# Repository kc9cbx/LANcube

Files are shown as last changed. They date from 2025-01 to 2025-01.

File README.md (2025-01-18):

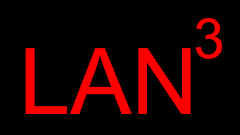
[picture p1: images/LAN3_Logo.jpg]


LAN3 is based on the design by Martin Aubé - 
[GitHub](https://github.com/aubema/lancube) - [WiKi](http://obsand.org/wiki/index.php?n=Prof.LANcube) - 
[Licensed under CC BY-SA 4.0 ](https://creativecommons.org/licenses/by-sa/4.0/)

## What is it?
LAN3 is a device that is designed to sample spectral and directional properties of lightsources in the urban or natural environments. In other words, it allows you to place this device on top of your vehicle, drive around and capture exeact phyisical location of each light source along the way, characterize each light's color temperature, and its spectrum. 

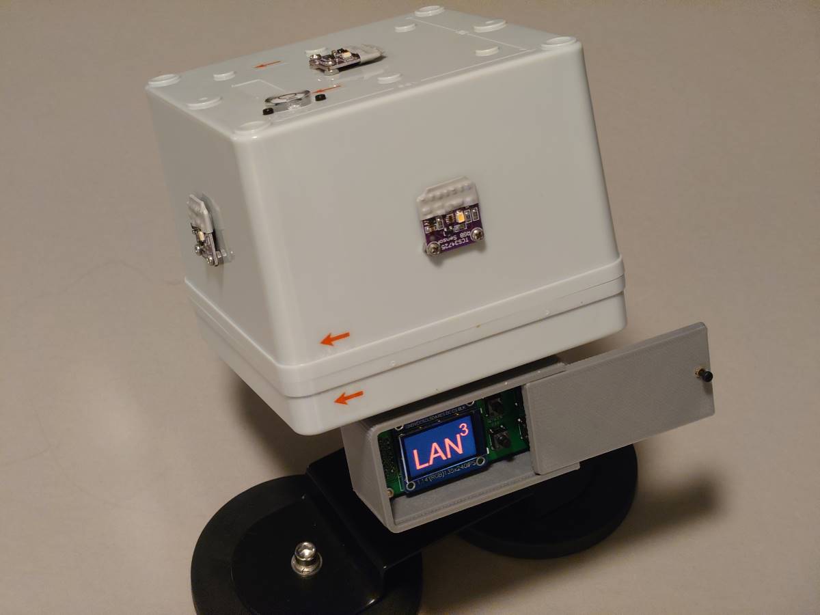
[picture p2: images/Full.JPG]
Full


## Changes in this version
This version of LAN3 exapands the original design with the follwing changes:
### Hardware Changes 
 - Addtion of the control panel - display and 4-button interface.
 - Addition of newly designed PCBs for both the control panel and the main part of the device.
 - Replacement of the external enclosure with the off-the-shelf box.
 - Transition to use of internal battery and battery monitoring for standalone operation.
 - Integration of the GPS on the interior of the device.

### Software Chages
 - Moving web server from Apache to Nginx.
 - Implementation of GPSd.
 - Automated time sync wiht GPS.
 - Addtion of full-featured web interface including device control, status management, and file management.
 - Change of how GPS status was reported from counting number of satelies to GPS mode. 
 - Requiring GPS Mode 3 (3D lock/high precision) to capture valid data.
 
## Build
The LAN3 is designed with off-the-shelf parts, available from Amazon, Ali Express, and may other places that sell DIY electronic components.

If you would like to build your own, head over the [Hardware](./Hardware/) section. There, you will find list of all the components, gerber files for PCBs, STL file for 3D printed part of the enclosure, and the assembly instructions.

For the software, pre-made IMG file is available that can be expanded onto an SD card. The [Software](./Softwre/) section has the details on how to provision your LAN3, allowing you to set your host and hotspot name. 

## Use
New interface is designed to make in-the-field data capture very simple:
1) Place the LAN3 on top of the vehicle. If possible, use a thin, dark fabric under the LAN3 to eliminate reflected light from impacting the measurements.
2) Press the "Power On" button.
3) Allow LAN3 to boot, to get a GPS lock, and to sync the time. The display will show "GPS Lock: Yes" and "GPS Time: Yes" when this is complete.
4) Press the "Start Measurement" button. The status on the display will show "Measuring".
5) Drive slowly around the area that you want to measure.
6) Once complete, press the "Stop Measurement" button.
7) Connect to the LAN3 hotspot, open your browser, go to the IP address on the LAN3 display, head over to the Files section, and download the file containing your measurements. 

## Data
Changes in this version of LAN3 were primarly focused on hardware and some of the software that supports that hardware. The core process of data capture has not changed. For data analysis and mapping after data has been captured, you will need to use the original LANCube analysis scripts. These are available on Martin Aubé's [GitHub](https://github.com/aubema/lancube) and in the [Original LANcube Archive](./Original_LANcube_Archive/) folder of this repo.

### Sample LAN3 Data
| Sensor | Year | Month | Day | Hour | Minute | Second | Latitude  | Longitude  | Altitude | GPSMode | Gain | AcquisitionTime(ms) | ColorTemperature(k) | MSI  | lux   | Red  | Green | Blue | Clear | Flag |
|--------|------|-------|-----|------|--------|--------|-----------|------------|----------|---------|------|---------------------|---------------------|------|-------|------|-------|------|-------|------|
| S1     | 2024 | 1     | 24  | 0    | 44     | 20.71  | 41.895442 | -87.654126 | 183.2    | 3       | 60   | 307.2               | 5875                | 0.6  | 49.57 | 2444 | 3094  | 2428 | 8301  | OK   |
| S2     | 2024 | 1     | 24  | 0    | 44     | 20.71  | 41.895442 | -87.654126 | 183.2    | 3       | 60   | 153.6               | 7201                | 0.67 | 37.14 | 745  | 1146  | 957  | 2825  | OK   |
| S3     | 2024 | 1     | 24  | 0    | 44     | 20.71  | 41.895442 | -87.654126 | 183.2    | 3       | 60   | 307.2               | 7820                | 0.7  | 31.84 | 1255 | 1996  | 1718 | 5100  | OK   |
| S4     | 2024 | 1     | 24  | 0    | 44     | 20.71  | 41.895442 | -87.654126 | 183.2    | 3       | 60   | 153.6               | 2429                | 0.49 | 24.89 | 1943 | 1236  | 1010 | 4064  | OK   |
| S5     | 2024 | 1     | 24  | 0    | 44     | 20.71  | 41.895442 | -87.654126 | 183.2    | 3       | 60   | 614.4               | 5933                | 0.59 | 28.73 | 2413 | 3388  | 2573 | 8782  | OK   |
| S1     | 2024 | 1     | 24  | 0    | 44     | 21.34  | 41.895512 | -87.65423  | 183.2    | 3       | 60   | 307.2               | 6572                | 0.63 | 40.83 | 1575 | 2414  | 1904 | 6225  | OK   |
| S2     | 2024 | 1     | 24  | 0    | 44     | 21.34  | 41.895512 | -87.65423  | 183.2    | 3       | 60   | 153.6               | 7077                | 0.65 | 47.39 | 793  | 1376  | 1105 | 3314  | OK   |
| S3     | 2024 | 1     | 24  | 0    | 44     | 21.34  | 41.895512 | -87.654231 | 183.2    | 3       | 60   | 307.2               | 7521                | 0.69 | 31.48 | 1433 | 2048  | 1774 | 5321  | OK   |
| S4     | 2024 | 1     | 24  | 0    | 44     | 21.34  | 41.895513 | -87.654231 | 183.2    | 3       | 60   | 153.6               | 2318                | 0.47 | 27.5  | 2116 | 1338  | 1070 | 4353  | OK   |
| S5     | 2024 | 1     | 24  | 0    | 44     | 21.34  | 41.895513 | -87.654231 | 183.2    | 3       | 60   | 614.4               | 6043                | 0.59 | 31.5  | 2523 | 3678  | 2796 | 9374  | OK   |
| S1     | 2024 | 1     | 24  | 0    | 44     | 21.97  | 41.895512 | -87.65423  | 183.2    | 3       | 60   | 307.2               | 7359                | 0.67 | 31.95 | 1050 | 1864  | 1517 | 4697  | OK   |
| S2     | 2024 | 1     | 24  | 0    | 44     | 21.97  | 41.895512 | -87.65423  | 183.2    | 3       | 60   | 153.6               | 6482                | 0.61 | 50.89 | 841  | 1433  | 1095 | 3419  | OK   |
| S3     | 2024 | 1     | 24  | 0    | 44     | 21.97  | 41.895512 | -87.65423  | 183.2    | 3       | 60   | 307.2               | 7106                | 0.68 | 24.99 | 1214 | 1639  | 1403 | 4311  | OK   |
| S4     | 2024 | 1     | 24  | 0    | 44     | 21.97  | 41.895512 | -87.654231 | 183.2    | 3       | 60   | 153.6               | 2426                | 0.46 | 32.85 | 2324 | 1521  | 1202 | 4794  | OK   |
| S5     | 2024 | 1     | 24  | 0    | 44     | 21.97  | 41.895513 | -87.654231 | 183.2    | 3       | 60   | 614.4               | 6041                | 0.59 | 26.54 | 2178 | 3128  | 2395 | 7925  | OK   |

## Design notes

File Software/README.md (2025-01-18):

## Setting up software and provisioning the LAN3 

#### Preparing the Card
Download the zip file containing the LAN3 SD card image from the Releases. Unzip the image – resulting file will be around 3.5Gb 

Follow the process outlined here: https://raspberrytips.com/create-image-sd-card/ to expand LAN3 image on to the SD card. 
 
To validate that your SD card was created correctly. Insert it into the LAN3 device and power it on. Keep in mind that first boot after card is created will take a while as image will re-size itself to fit the card and then reboot. If your GONet hardware is working correctly and the SD card was imaged correctly, after a couple of minutes, the display will turn on and you will see, on the very first line, “PROVISION” followed by a version number. 
 
#### Provisioning
Press the power off button to turn off the device. Once all lights have turned off, remove the SD card and place it back in your computer.
 
Download and open the provided LAN3Config.conf file. In the file, update the text in the quotes on the first line. This will set the name for your LAN3. For example, to name the LAN3 MyLAN3001, the first line should look like this:
HostName="MyLAN3001"

At this time, only the first line is used, so you can disregard the rest of the file.
 
Once you have the LAN3Config.conf updated, copy it on your LAN3 SD card into /fsboot/.
 
Place the SD card into the LAN3 and turn it on. It may take several minutes for provisioning to complete, as multiple automatic reboots are required, so please be patient.
 
Once provisioning is complete, the display will come on and you will see your LAN3 name at the very first line, indicating that provisioning was successful.

#### Hotspot
After provisioning, LAN3 will create its own hotspot, with the same name as the LAN3. When this happens, using the examle from above, you will see “HOTSPOT: MyLAN3001” on the display. You can connect to that hotspot using the password “Remote4LAN3” (capitalization matters!)

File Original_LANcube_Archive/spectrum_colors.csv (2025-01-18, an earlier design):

r/g | b/g | i/g | ULOR | tech
2.64 | 0.60 | 0.07 | 0.03 | HPS
2.50 | 0.65 | 0.07 | 0.03 | HPS
2.79 | 0.59 | 0.16 | 0.03 | HPS
3.47 | 0.74 | 0.25 | 0.03 | HPS
2.50 | 0.77 | 0.11 | 0.03 | HPS
2.27 | 0.84 | 0.50 | 0.03 | HPS
2.21 | 0.67 | 0.07 | 0.03 | HPS
2.84 | 0.71 | 0.16 | 0.03 | HPS
0.87 | 0.98 | 0.22 | 0.05 | MH4000
0.80 | 0.54 | 0.15 | 0.10 | MV
1.01 | 0.57 | 0.36 | 0.10 | MV
5.43 | 0.64 | 0.17 | 0.00 | LED1500
1.94 | 0.42 | -0.11 | 0.00 | LED1650
1.64 | 0.38 | -0.08 | 0.00 | LED1650
3.87 | 0.47 | 0.13 | 0.00 | LED1800
2.65 | 0.43 | -0.10 | 0.00 | LED1800
2.37 | 0.44 | -0.15 | 0.00 | LED1800
3.42 | 0.51 | 0.03 | 0.00 | LED1800
2.91 | 0.49 | 0.01 | 0.00 | LED1800
1.85 | 0.56 | 0.03 | 0.00 | LED2200
1.99 | 0.75 | 0.04 | 0.00 | LED3000
1.87 | 0.69 | 0.02 | 0.00 | LED3000
0.81 | 0.51 | -0.11 | 0.00 | LED3500
1.04 | 0.77 | -0.03 | 0.00 | LED4000
1.00 | 0.67 | -0.06 | 0.00 | LED4000
0.95 | 0.58 | -0.09 | 0.00 | LED4000
1.21 | 0.89 | 0.02 | 0.00 | LED5000
0.99 | 0.84 | 0.02 | 0.00 | LED5500
0.60 | 0.81 | -0.09 | 0.00 | LED5500
3.38 | 0.83 | 3.65 | 0.30 | INC2550
2.79 | 0.82 | 2.37 | 1.30 | INC2550

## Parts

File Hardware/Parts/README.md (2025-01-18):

| Part                                                                                     | Quantity | Source(s)                                                                                                          |
|------------------------------------------------------------------------------------------|----------|--------------------------------------------------------------------------------------------------------------------|
| MAIN BOARD                                                                               |          |                                                                                                                    |
| Main Board PCB                                                                           | 1        | See Hardware folder for gerber files                                                                               |
| SparkFun LiPo Fuel Gauge (MUST GET FROM SPARKFUN, LOTS OF FAKE ONES ELSEWHERE)           | 1        | https://www.sparkfun.com/products/20680                                                                            |
| GT-U7 GPS Module                                                                         | 1        | https://www.amazon.com/gp/product/B08ZSMPPP6                                                                       |
| Flexible 15 pin Cable,150mm, 1mm Pitch (FPC/FFC type - same as raspberry pi HQ camera)   | 1        | https://www.amazon.com/dp/B07RWQQHKY                                                                               |
| 15 Position FFC, FPC Connector Contacts, Vertical - 1 Sided 0.039" (1.00mm) Through Hole | 1        | https://www.digikey.com/en/products/detail/amphenol-icc-fci/SLW15S-1C7LF/1002258                                   |
| Electronic Power Switch with Reverse Voltage Protection, LV                              | 1        | https://www.pololu.com/product/2808 OR https://www.digikey.com/en/products/detail/pololu-corporation/2808/10450608 |
| 330uF 25V 8X12MM Electrolytic Capacitors                                                 | 2        | https://www.amazon.com/gp/product/B09TQTV372                                                                       |
| Raspberry Pi 4 B - at least 2GB Model                                                    | 1        | https://www.sparkfun.com/products/15446                                                                            |
| 2x20 Extra Tall Stacking Headers for Pi                                                  | 1        | https://www.amazon.com/gp/product/B01EF42LTY                                                                       |
| JST XH 2.54mm 7 Pin Male Connector and 26AWG Female Connector Plug with Wire             | 5        | https://www.amazon.com/gp/product/B0CF26XWJ4                                                                       |
| Extra Tall Stacking Header for Raspberry Pi - 2x20  Header                               | 1        | https://www.amazon.com/gp/product/B01EF42LTY                                                                       |
| USB-C charger and Boost Converter Module                                                 | 1        | https://www.amazon.com/dp/B09YD5C9QC                                                                               |
| 11mm Heatsink  for Raspberry Pi 4 (P165-B)                                               | 1        | https://www.amazon.com/dp/B08N5VZN8R OR https://geekworm.com/products/p165-b                                       |
| JST-PH 2.0 Male and Female Connector Cable                                               | 1        | https://www.amazon.com/dp/B07NWD5NTN                                                                               |
|                                                                                          |          |                                                                                                                    |
| CONTROL BOARD                                                                            |          |                                                                                                                    |
| Control Board PCB                                                                        | 1        | See Hardware folder for gerber files                                                                               |
| 3D printed case with sliding cover for the control board                                 | 1        | See Hardware folder for STL file                                                                                   |
| ST7789 TFT IPS Display Module 1.14in, 135x240, 8Pin                                      | 1        | https://www.amazon.com/dp/B07ZQ1C712                                                                               |
| 15 Position FFC, FPC Connector Contacts, Vertical - 1 Sided 0.039" (1.00mm) Through Hole | 1        | https://www.digikey.com/en/products/detail/amphenol-icc-fci/SLW15S-1C7LF/1002258                                   |
| 6x6x8mm Micro PCB Momentary Push Button                                                  | 4        | https://www.amazon.com/dp/B07HCM7XK8                                                                               |
|                                                                                          |          |                                                                                                                    |
| EXTERNAL ENCLOSURE AND RELATED HARDWARE                                                  |          |                                                                                                                    |
| 125x125x100mm (5x5x4in) Junction Box                                                     | 1        | https://www.amazon.com/dp/B071JLC6C5                                                                               |
| RG178 SMA Female to U.FL Pigtail                                                         | 1        | https://www.amazon.com/gp/product/B098QH631G OR https://www.sparkfun.com/products/9145                             |
| Active GPS Antenna - SMA Male Connector                                                  | 1        | https://www.amazon.com/gp/product/B0BWDJJLPN OR https://www.sparkfun.com/products/177                              |
| 1/4"-20 Wall/Table Mount                                                                 | 1        | https://www.amazon.com/gp/product/B09XMKHQZP                                                                       |
| Magnetic Action Camera Mount, Heavy-Duty (2 * 88mm Base）                                 | 1        | https://www.amazon.com/gp/product/B09VS2LR8G                                                                       |
| 8000mAh 126090 battery with PH 2.54 JST Connector                                        | 1        | https://www.amazon.com/dp/B0C1HFRBFV                                                                               |
| USB-C Bulkhead connector                                                                 | 1        | https://www.amazon.com/dp/B0B7QYG313                                                                               |
| TCS34725 RGB Light Color Sensor                                                          | 5        | https://www.amazon.com/dp/B08L7MS8L4                                                                               |
| USB-C to USB-C 1ft 90 Degree Cable                                                       | 1        | https://www.amazon.com/gp/product/B0B5QJTT8M                                                                       |
| Triangular bubble level with mounting holes                                              | 1        | https://www.amazon.com/gp/product/B09NL2V31X                                                                       |
| Male Pin Header Strip (2.54 mm)                                                          | 1        | https://www.amazon.com/dp/B07PKKY8BX                                                                               |
| USB C to USB C Cable  1ft  90 Degree Cable                                               | 1        | https://www.amazon.com/gp/product/B0B5QJTT8M                                                                       |
| ABS plastic sheet                                                                        | 1        | https://www.amazon.com/gp/product/B0BM8WHLNT                                                                       |
| 70mm x 1m  heat shrink tube                                                              | 1        | https://www.amazon.com/gp/product/B07YTKVYYF                                                                       |
| SD card of your choice, minimum 32Gb, Class 10                                           | 1        |                                                                                                                    |

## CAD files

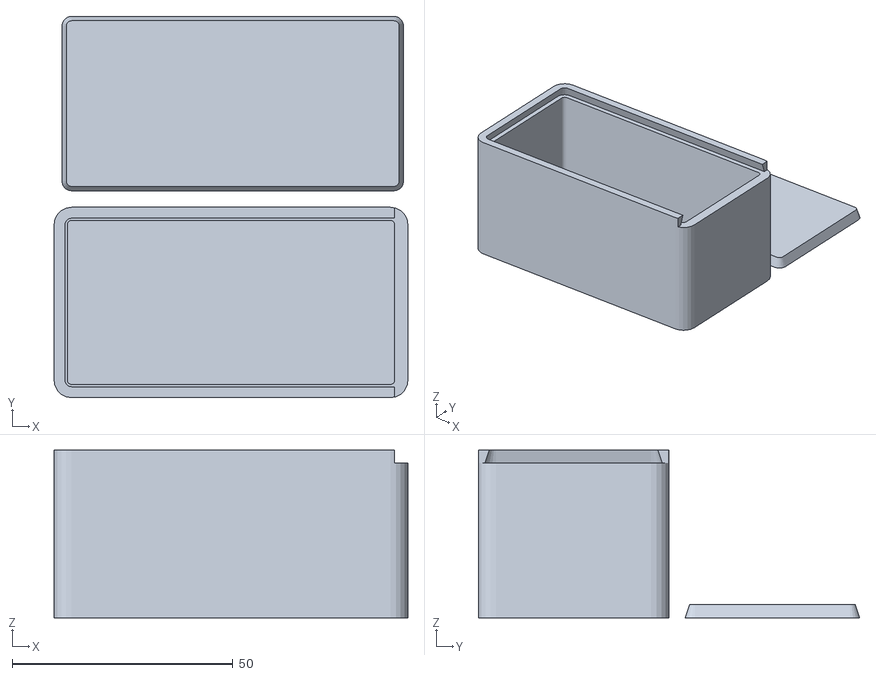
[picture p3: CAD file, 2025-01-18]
Hardware/Control Board Enclosure/LAN3_Control_Board_Enclosure.stl
80.1 x 86.3 x 38.0

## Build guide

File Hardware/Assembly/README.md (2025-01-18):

## Build and Assembly

Please carefully review the included pictures to get an idea of what the final product should look like.
Full
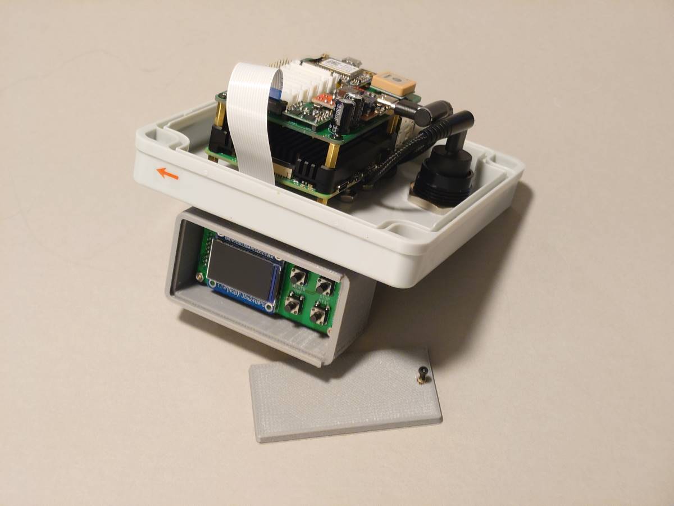
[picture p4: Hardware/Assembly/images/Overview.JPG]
Overveiw

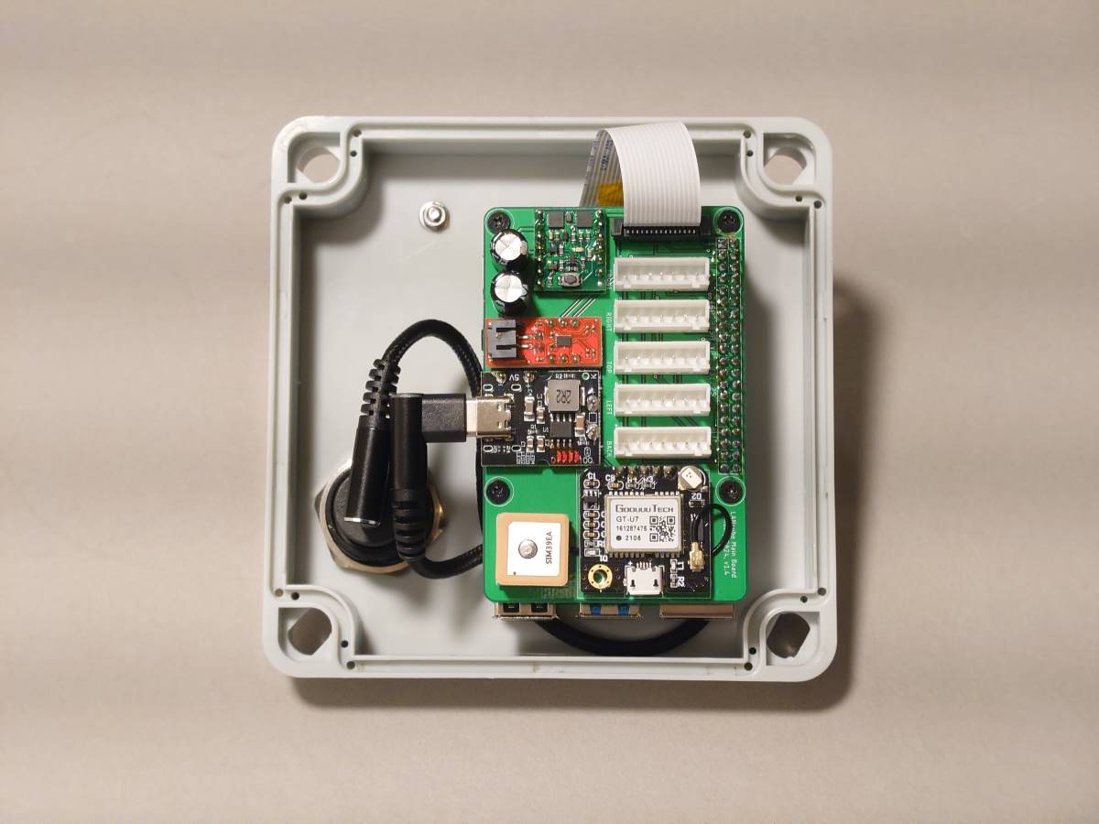
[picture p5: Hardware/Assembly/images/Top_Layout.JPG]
Top Layout

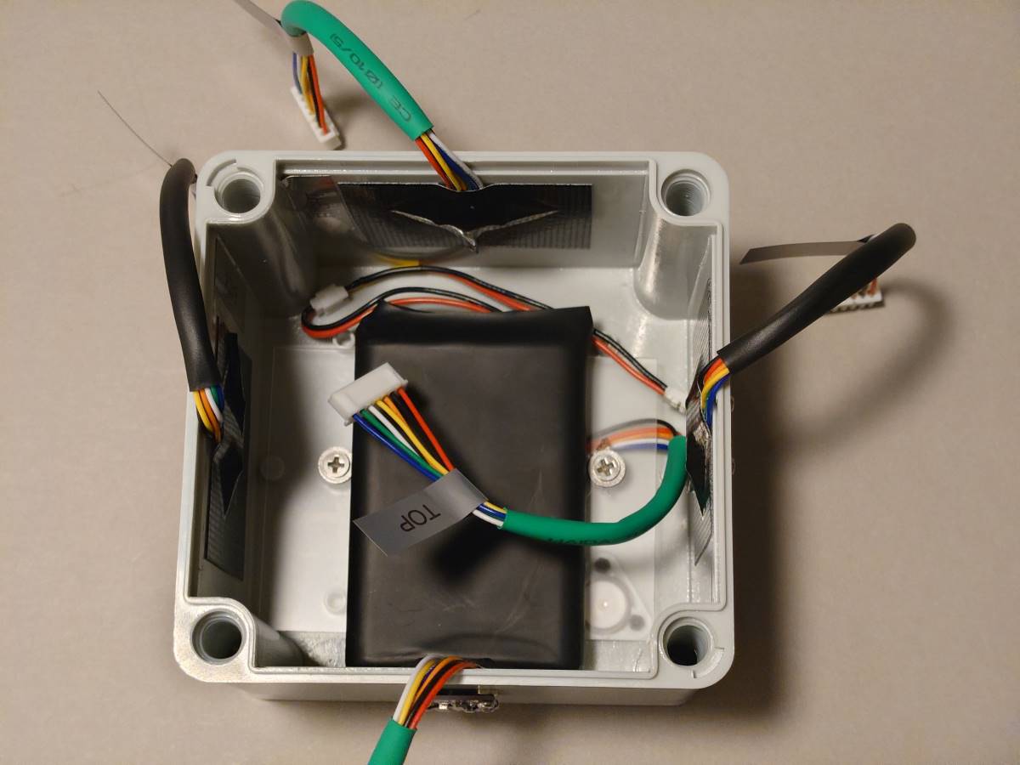
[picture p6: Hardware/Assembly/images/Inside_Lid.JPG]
Inside Lid

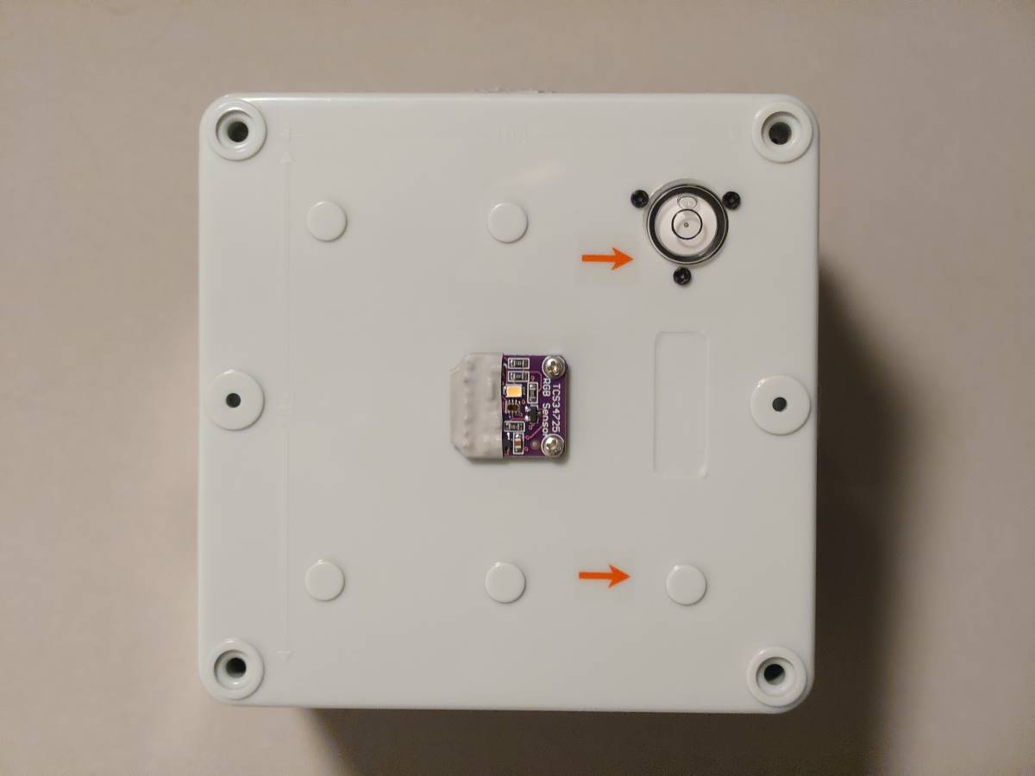
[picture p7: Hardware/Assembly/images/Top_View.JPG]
Top View

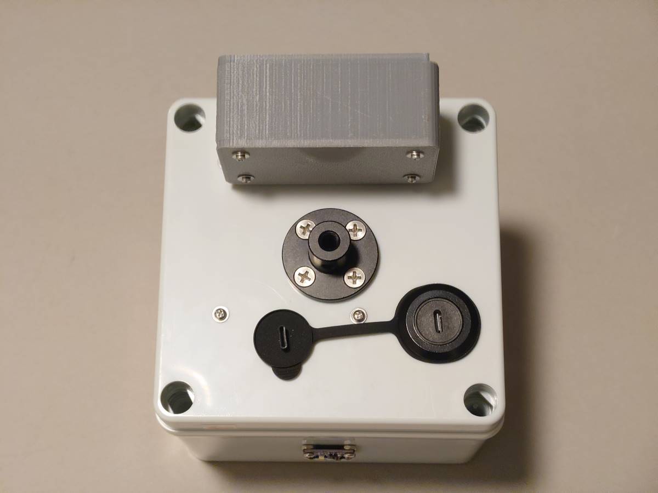
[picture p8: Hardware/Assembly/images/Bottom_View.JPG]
Bottom View

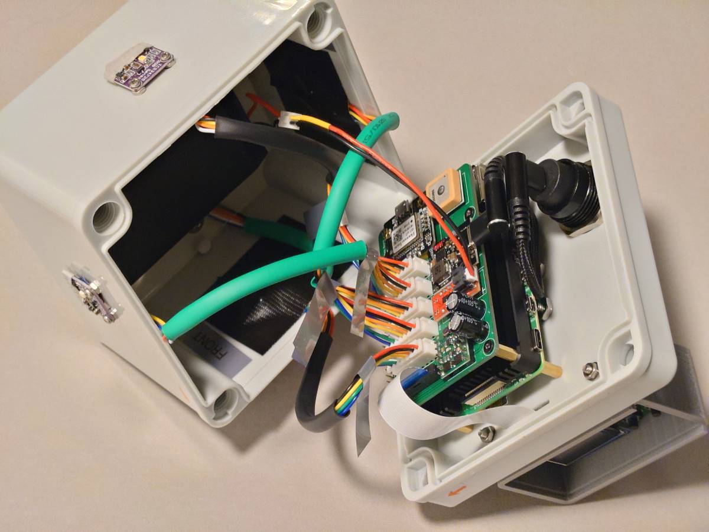
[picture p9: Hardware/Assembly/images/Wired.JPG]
Wired


#### Before you start
 - Use the gerber files in the Hardware folder and order control and main PC board from the board house of your choice (JLCPCB, PCB GOGO, PCB WAY, etc.) 
 - Obtain all the parts listed in the Parts section
 - 3D print the enclosure for the control board
 
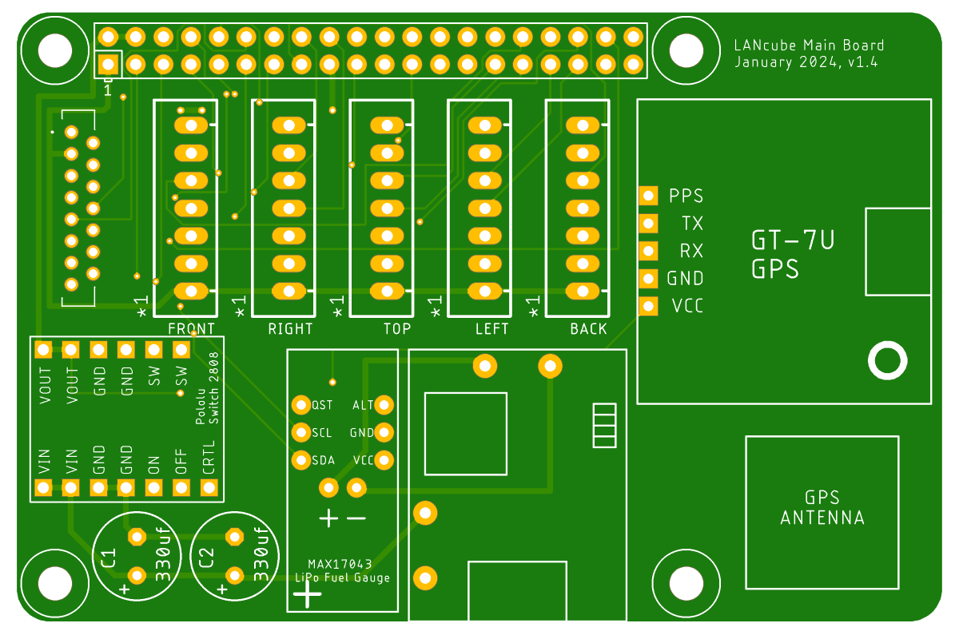
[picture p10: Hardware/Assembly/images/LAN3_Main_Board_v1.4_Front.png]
Main PCB Front

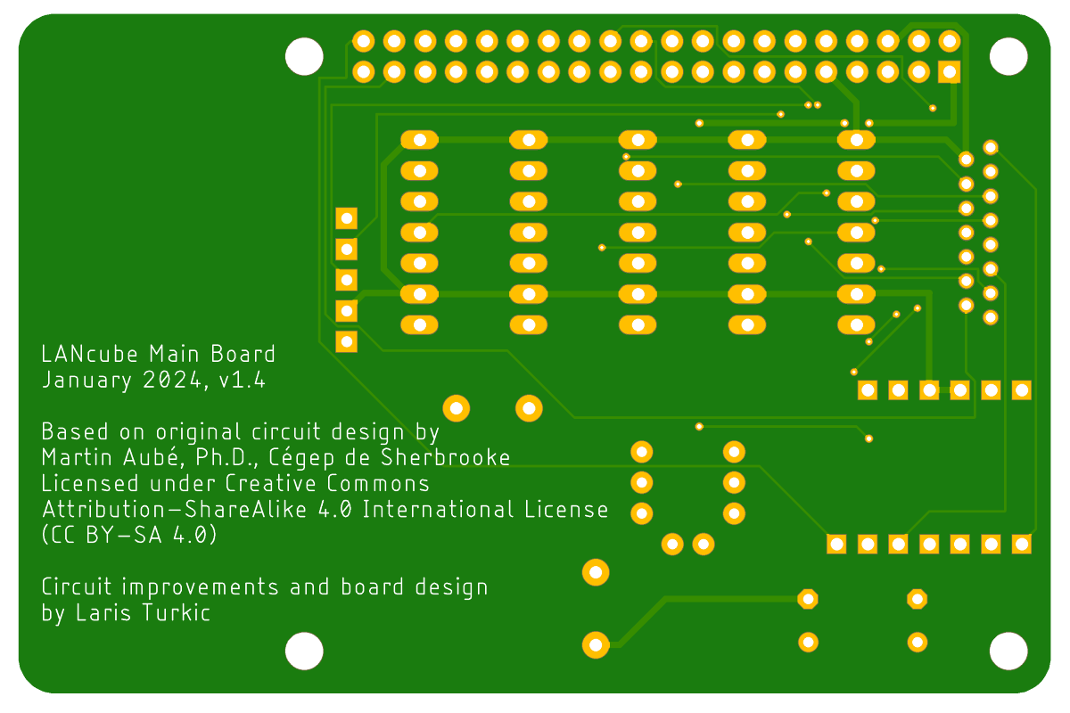
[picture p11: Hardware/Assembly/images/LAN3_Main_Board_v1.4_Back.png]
Main PCB Back

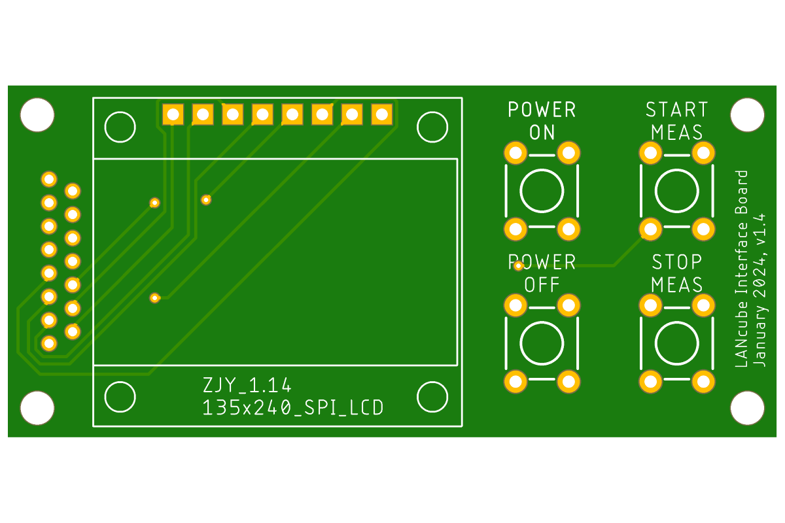
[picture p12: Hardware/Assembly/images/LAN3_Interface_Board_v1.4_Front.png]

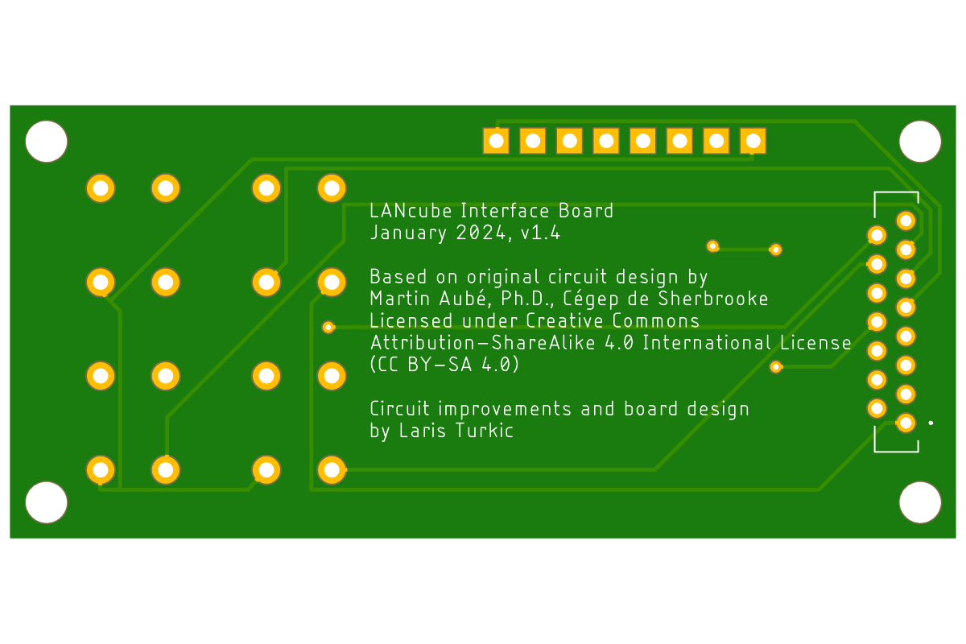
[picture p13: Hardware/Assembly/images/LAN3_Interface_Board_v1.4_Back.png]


#### Start with assembling the control panel/control board.
 - Drill and cut necessary holes/openings 
   - Place the blank control PCB on the bottom of the 3D printed enclosure and mark off where to drill for PCB standoffs; drill the necessary holes.
   - About 1/2 way down the long side of the control board enclosure, cut in a slot to feed through  the flat ribbon cable - about 3mm width and length that is about double the width of the FCC cable. The side where you cut in the slot will be the top of the control board enclosure.
   - On this same side of the enclosure, drill two holes for screws that will be used to mount the control panel enclosure to the main box
 - Solder all the components
   - Place and solder the 4 pushbuttons onto the PCB
   - Solder on the header pins onto to the display
   - Solder the display onto the front PCB
   - Insert the FCC connector from the back of the board and solder it in place
 - Assemble the control panel
   - Mount the PCB onto standoffs
   - Feed through the screws that will be used to mount the control panel assembly to the main box, and secure them in place with nuts
   - Connect ribbon cable to the FCC connector on the back of the control board
   - Feed the cable trough the slot on the box
   - Slide the PCB on standoffs and secure it to the bottom of the box
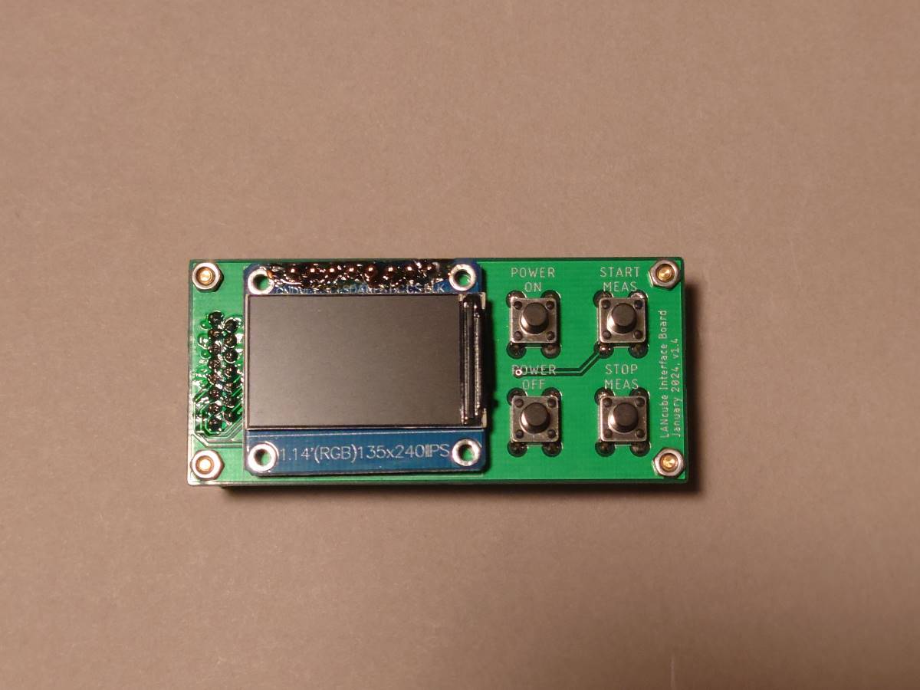
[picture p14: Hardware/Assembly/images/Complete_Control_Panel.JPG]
Complete Control Panel

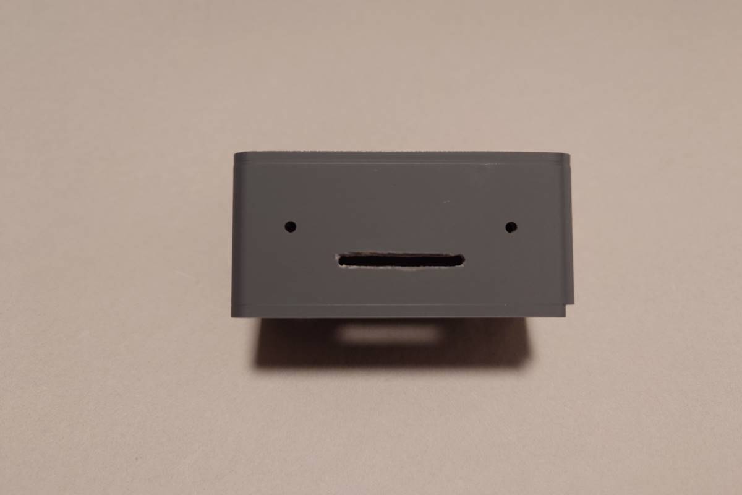
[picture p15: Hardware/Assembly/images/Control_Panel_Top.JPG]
Control Panel Top

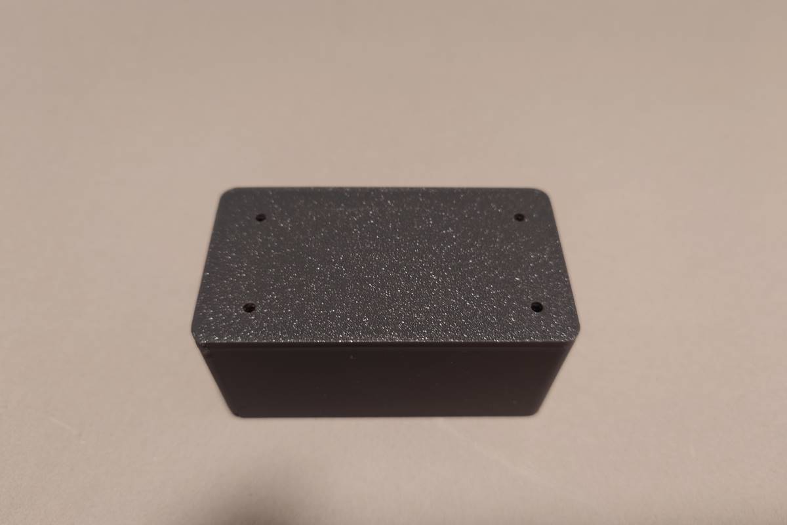
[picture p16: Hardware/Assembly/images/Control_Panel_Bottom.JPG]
Control Panel Bottom


#### Assemble the main board
 - Prepare all components
   - Solder header pins onto the GPS module
   - Solder header pins onto the fuel gauge - 1 set of 2 pins, and tw2 sets of 3 pins
   - Solder header pins onto the charging board - you will need 4 individual pins
   - Solder header pins onto the Pololu electronic switch - one set of 6 pins and one set of 7 pins
 - Solder everything onto the main board
   - Start with raspberry pi pin headers. To determine correct length, first, mount 20mm standoffs onto the bottom of the main board. Push the headers onto the raspberry pi and then place the main PCB over the headers. At this point, take a moment to verify that there is a 3-4mm clearance between the main board and the metal of the USB and ethernet port on the Pi - we want to make sure that nothing will short out once components are soldered onto the main board.
   - With everything in place like this, solder the headers to the main board. Once soldered, trim off the excess from the top.
   
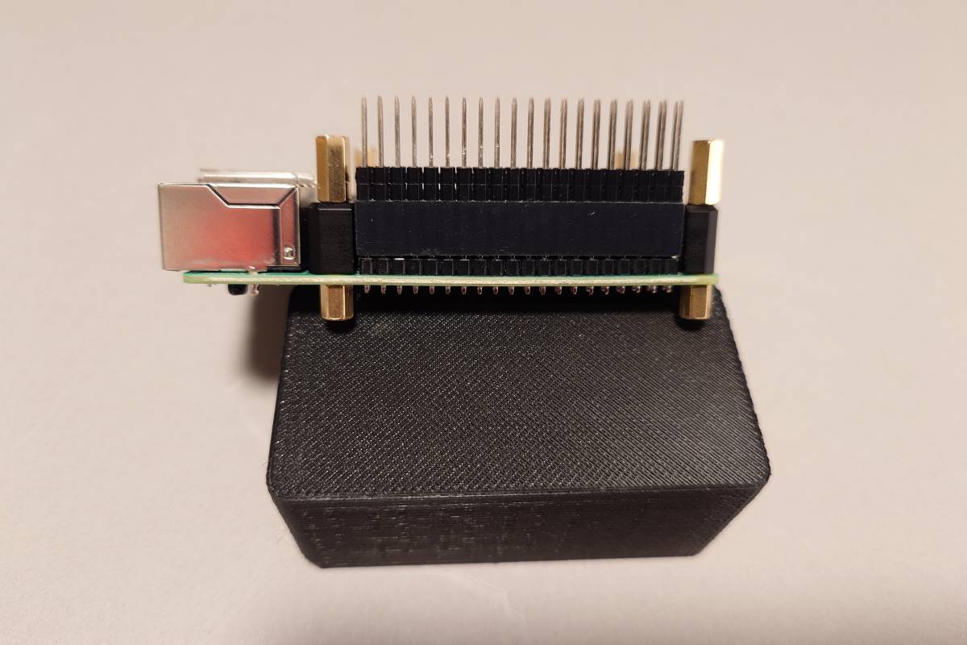
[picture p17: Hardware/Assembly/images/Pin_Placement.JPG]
Pin Placement

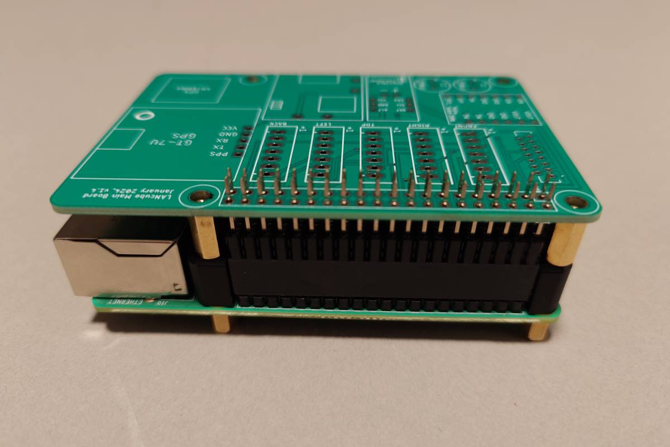
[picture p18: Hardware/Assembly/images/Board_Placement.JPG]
Board Placement


   - Remove the main board from the pi
   - Solder the FCC connector
   - Solder the 5 7-pin connectors
   - Solder the GPS module
   - Solder the electronic switch
   - Solder the two capacitors - pay attention to polarity
   - Solder the fuel board
   - Solder the charging board
   
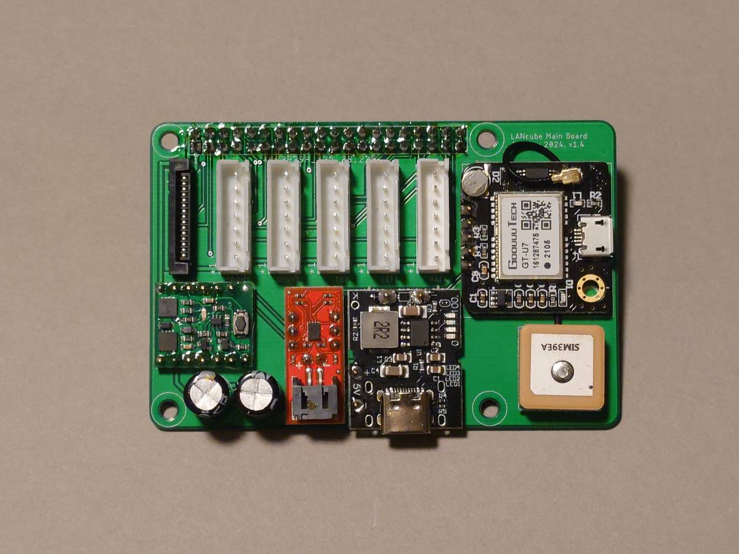
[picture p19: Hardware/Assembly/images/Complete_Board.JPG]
Complete Board


#### Prepare the sensors
 - Sensor wiring is relatively simple - it is straight through, pin for pin. Pin 1, as marked on the main board, connects to VIN on the sensor, Pin 2 is wired to GND on the sensor, etc. Please take a look at the picture on what the finished sensor looks like. 
 - Also, please note the orientation of the soldered wires - they are turned inwards, towards the center of the sensor. While this is not crucial, this orientation makes it easier to hide the wires once sensors are mounted.
 - Lastly, you can use heat shrink to protect the solder points on the sensor module board, just be careful to not cover up or obstruct the sensor.

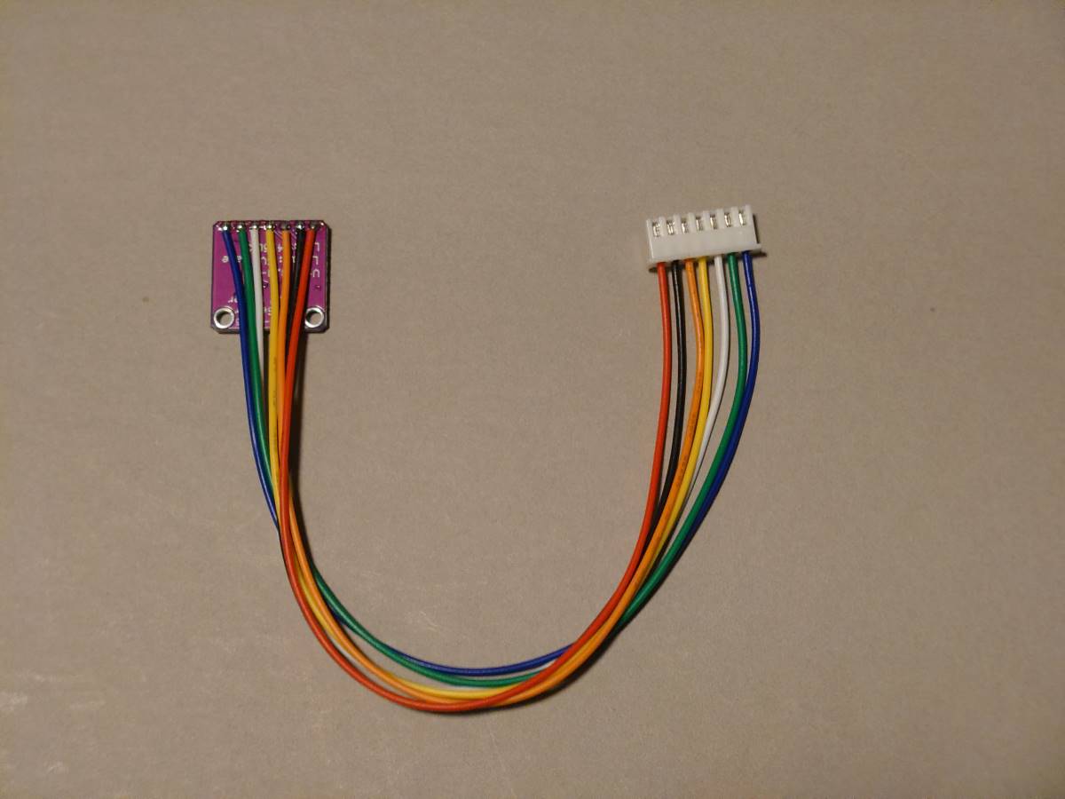
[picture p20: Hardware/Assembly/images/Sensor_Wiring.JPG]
Sensor Wiring


#### Prepare the main box
 - Before assembly, drill all the necessary holes
   - On the bottom/lid drill 4 holes for the Raspberry Pi, 4 holes for tripod mount (centered), 2 holes needed to mount the control panel, hole for the USB C bulkhead connector, and lastly, the slot for the ribbon cable
   - On the main part of the box drill three hole for each sensor - one that is large enough to feed through the harness connector and two needed to mount the sensor. When determining the mounting location, mark the hole placement so that sensor is placed in the center of that side of the box. 
   - Optional - if used, drill the necessary holes to mount the bubble level
   
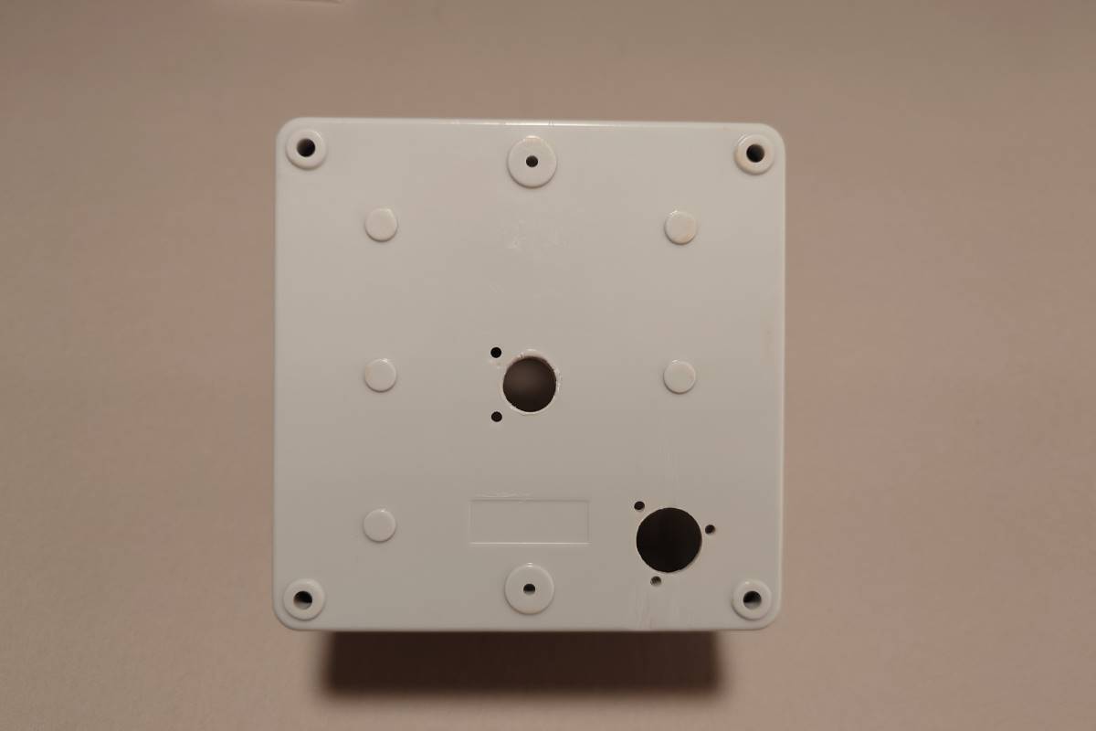
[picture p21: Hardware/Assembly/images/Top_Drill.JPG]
Top Drill

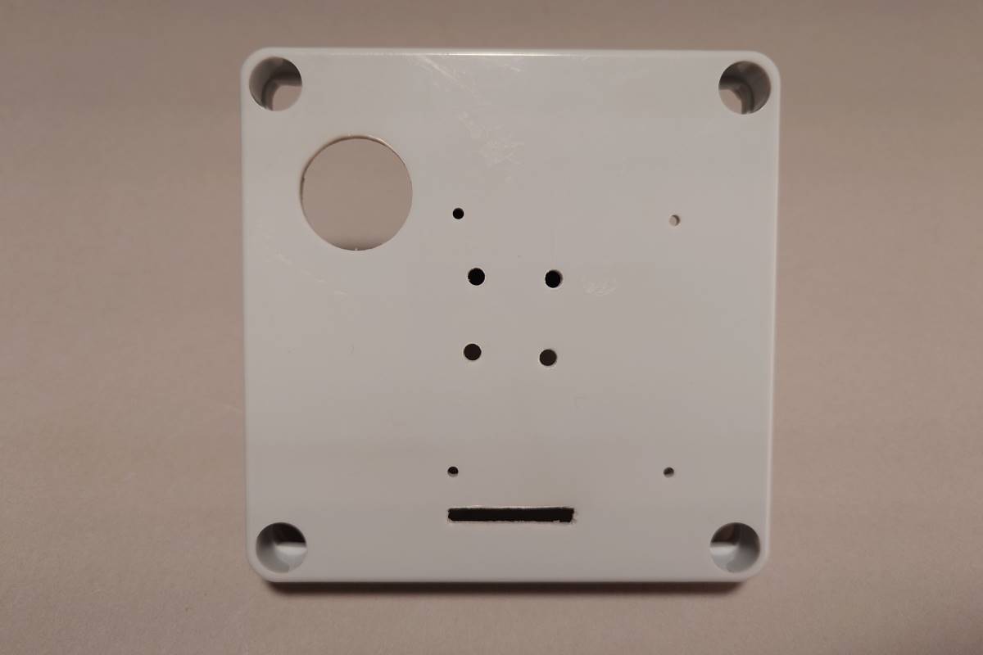
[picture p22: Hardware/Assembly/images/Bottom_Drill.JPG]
Bottom Drill

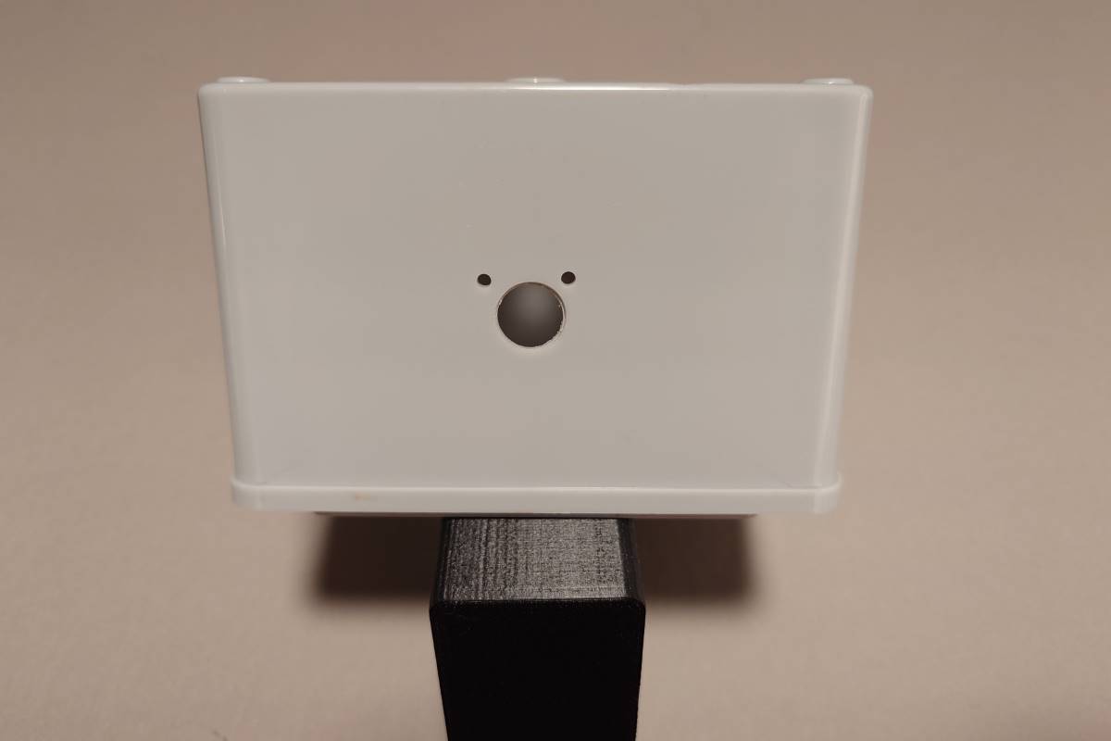
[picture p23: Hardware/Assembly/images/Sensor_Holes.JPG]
Sensor Holes


#### Determine which side/sensor will be the front and MARK IT.
 - When choosing the front, it is very convenient to choose the side that is either to the left or the right of the side where control panel will be mounted. As LAN3 is most often used on the top of the vehicle, choosing one of these sides will make it easy to access controls from either driver or the passenger side of the vehicle, without having to remove it from the roof.
 - Draw arrows that point towards the front, on both the inside and the outside of the LAN3

#### Mount all the sensors
 - Mount the prepared sensors to the box using short standoffs or alternatively, nuts as spacers.
 - Mark the end of each cable harness with the side on which sensor is mounted - top, front, back, left, and right
 - Once sensor is mounted, cover the opening for the harness and mounting screws with black Gorilla tape. This will prevent light from the inside of the box from reaching the sensor.
   
#### Mounting the Battery and GPS antenna
 - This is a tricky one, as both are mounted to the top of the main box. We will use the two brass insets at the top of the box to do this. You will need piece of plastic that is slightly smaller than the inner dimension of the box. You can use ABS, acrylic, or really any type of plastic of the right size. Drill 2 holes into the plastic so that they align with brass insets. It is recommended that you obtain countersunk screws for this.
 - For the GPS antenna, you will sandwich it between the box and the plastic sheet, then screw the plastic sheet to the box. As battery will go over the top of the screws, place a piece of thick/heavy tape over the screws to protect the battery - black Gorilla tape works great for this. 
 - Before the battery is installed, it needs to be protected from physical damage. Use 70mm heat shrink to do this, but be VERY CAREFUL when applying heat shrink to not overheat the battery.
 - Once battery is protected, use double sided tape + gorilla tape to secure the battery to the top of the box

#### Mount components to the lid 
 - Install the tripod mount
 - Install the USB C bulkhead connector
 - Feed through the ribbon cable and mount the control panel box
 - Finally, mount the Raspberry Pi, using standoffs that are tall enough to keep it away from the protruding screws 
 
#### Connect the GPS
  - Use the extension cable to connect the GPS antenna to the U. FL/I-PEX connector on the GPS board

#### Connect the USB C
 - Connect the USB C connector on the charging board to the USB-C bulkhead connector using the right-angle USB-C cable
 
#### Connect the control panel
 - Connect the ribbon cable from the control panel to the FFC connector on the main board
 
#### Connect all the sensors
 - Connect each sensor to the corresponding connector on the main board - each connector is labeled on the main board. Incorrect sensor placement will give you incoherent results.

#### Finally, connect the battery - EXCERCISE EXTREME CAUTION WITH BATTERY POLARITY
 - Please note that JST battery connectors are NOT STANDARD, not all are wired in the same, and may be wired EXACTLY BACKWARDS from what you need. Before connecting the battery, please verify that positive/red wire is closest to the capacitors. Main board under the fuel gauge also has "+" marking on the correct side. If your battery/connector are backwards, you can use a thin blade to carefully lift up the clip holding each wire in the connector and swap their positions to get correct polarity.
 - Once you've verified the polarity, connect the battery
 - As the final hardware check, connect a charger to the USB-C connector on the outside of the case, and you should see charging board battery level LEDs turn on

With the hardware complete, go to the software section to learn how to prepare the SD card.

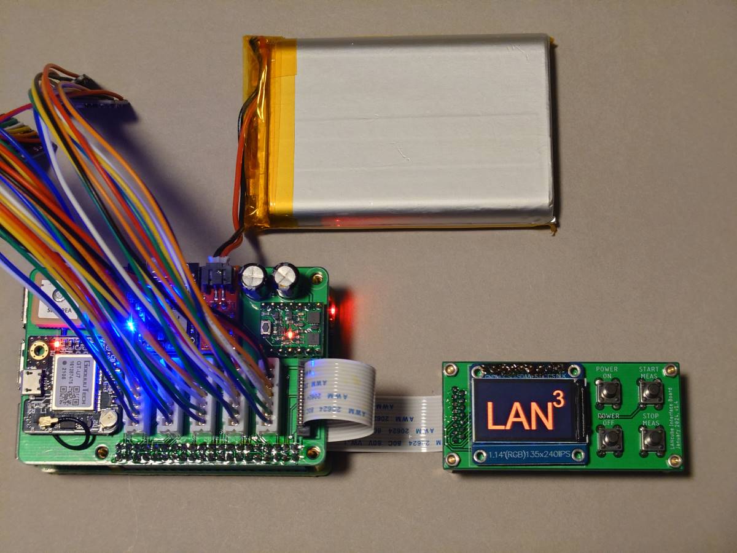
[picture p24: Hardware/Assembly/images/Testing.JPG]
Testing


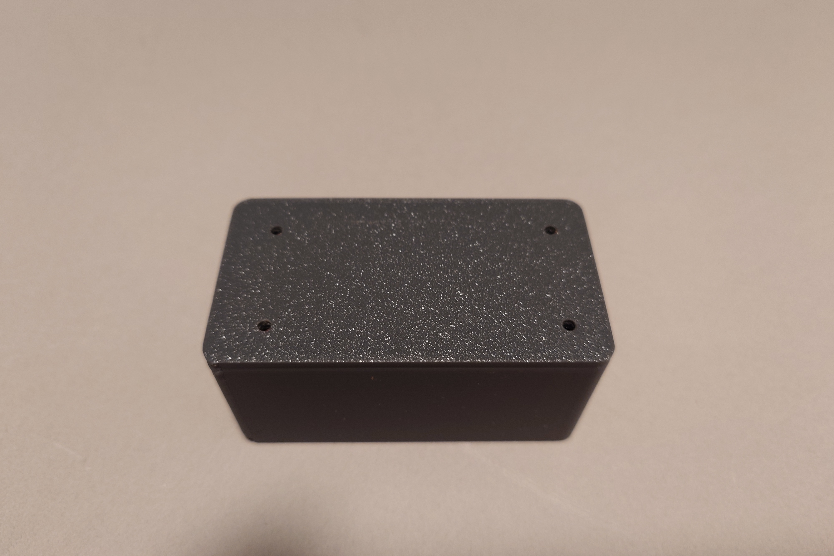
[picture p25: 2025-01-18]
Hardware/Assembly/images/Originals/Control_Panel_Bottom.JPG
